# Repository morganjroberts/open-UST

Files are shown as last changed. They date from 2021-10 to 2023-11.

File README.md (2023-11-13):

<p align="center">
  
</p>

# **open-UST:** An Open Source Manufacturing Framework for a Low-cost Ultrasound Tomography Research System.

There is a high barrier to entry for researchers starting ultrasound tomography (UST) experiments: UST hardware is not available off the shelf, and custom systems are expensive.
The goal of the open-UST project is to **lower the barrier to entry for experimental UST researchers**, by providing a manufacturing framework that allows end users to build their own UST transducers in-house.

<p align="center">
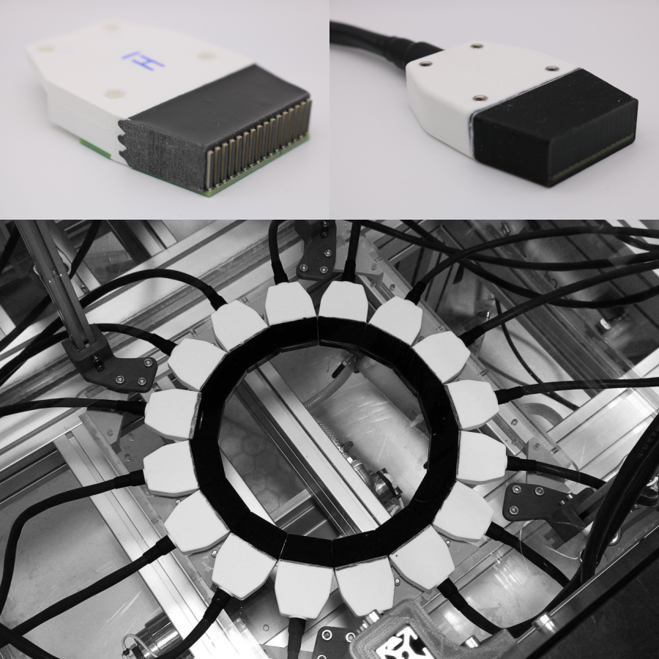
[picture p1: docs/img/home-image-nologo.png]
  
</p>

open-UST is part of an ongoing research project, guided by three objectives:

1. High accessibility for end users.
2. Nominal acoustic behaviour that supports UST imaging research.
3. Low inter-element variation (IEV) in acoustic behaviour.

## Features

- **Simple equipment requirements:** No specialist equipment required, only a 3D-printer, vacuum chamber and standard workshop tooling.
- **Low material cost:** ~£2k (excluding DAQ hardware) for a 256-element system.
- **Modular:** Both 2D and 3D imaging setups can be configured. 
- **Low interelement variation**: Recent testing showed that the individual sensing elements have uniform acoustic behaviour.
- **Other:**
  - Fully waterproof
  - Electromagnetically shielded
  - Transducer modules feature threaded mounting points for repeatable positioning
  - Includes option for a modular interface with the ITT Cannon DL5-260P connector (compatible with Verasonics)

## Hardware Distribution and Documentation

To access the design and manufacture files, clone this repository locally:

```
git clone https://github.com/morganjroberts/open-UST
```

The design and manufacture files are located in the `hardware-distribution` directory.

For the accompanying manufacturing documentation, please visit [morganjroberts.github.io/open-UST](https://morganjroberts.github.io/open-UST/).

## Citing open-UST

Please cite this article if you use open-UST in your research:

```
@article{roberts2023open,
  title     = {open-UST: An Open-Source Ultrasound Tomography Transducer Array System},
  author    = {Roberts, Morgan and Martin, Eleanor and Brown, Michael D and Cox, Ben T and Treeby, Bradley E},
  journal   = {IEEE Transactions on Ultrasonics, Ferroelectrics, and Frequency Control},
  year      = {2023},
  publisher = {IEEE},
  doi       = {10.1109/TUFFC.2023.3280635}
}
```

## Contact

open-UST is an ongoing research project from the [Biomedical Ultrasound Group](https://bug.medphys.ucl.ac.uk/) (University College London).

For questions, suggestions and feedback, please contact Morgan Roberts at [morgan.roberts.18@ucl.ac.uk](mailto:morgan.roberts.18@ucl.ac.uk).

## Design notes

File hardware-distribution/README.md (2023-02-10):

# Hardware Distribution

## CAD and 3D-printing files
- The CAD source files were generated in Fusion 360: [Download Fusion 360 for Education](https://www.autodesk.com/education/edu-software/overview?sorting=featured&filters=individual).
- The CAD source files are also available as `.step` files.
- The 3D-printed components have been exported as `.stl` files.

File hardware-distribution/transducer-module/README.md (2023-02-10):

# Transducer Module 

<p align="center">
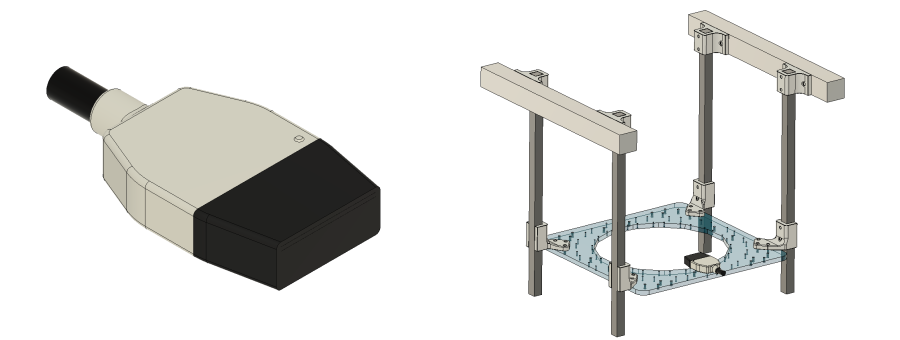
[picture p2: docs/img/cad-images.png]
  
</p>

The transducer module source files are found within `transducer-module.f3d`. The CAD file is split into the following components:

| Component | Type | Description |
|---|---|---|
| PZT Elements | Transducer part | PZT elements with matching layers.|
| PCB | Transducer part | Interconnect PCB used to interface cable with PZT elements. |
| Backing Layer | Transducer part | Cast behind the PZT elements to provide damping. |
| SMT Header | Transducer part | Surface mount header strip soldered to interconnect PCB to mate with cable IDC connector. |
| IDC connector | Transducer part | Crimped onto ribbon cable, mates with SMT header. |
| Housing | Transducer part | 3D-printed backbone of the transducer module. PCB and backing layers are bonded to this. Cable fixed to this. |
| Ribbon Cable | Transducer part | Round bundled ribbon cable in overall sheath. IDC connector is crimped to this. |
| Cover | Transducer part | Completes the housing after the cable is fixed in place. |
| PZT Alignment Mould | Sacrifical custom tooling | Aligns the PZT elements during manufacture, gets dissolved in water to remove it. |
| Clamp | Re-usable custom tooling | Clamps the housing to the base plate during backing layer casting. |
| Base Plate | Re-usable custom tooling | Holds the PCB, housing, and PZT alignment mould together during manufacture. |
| Mounting nuts | Transducer part | Glued into the housing, used to fix the transducer module to the array mounting plate. |
| Coatings | Transducer part | Epoxy and polyurethane coatings to protect the transducer modules. |
| Coating Moulds | Sacrificial custom tooling | Used for casting the coating layers around the transducer module. |
| Inclined Jig | Re-usable custom tooling | Used to hold the base plate at a 45 degree angle during application of conductive epoxy to the PZT electrodes. |
| Rigid Aperture Support | Additional part | Used to mount the transducer modules into a 2D ring array configuration. |
| Testing Mount | Additional part | Used to hold a single transducer module vertically during cable entry-point sealing, or electrical input impedance measurement. |
| Shielding Templates | Re-usable custom tooling | 2D templates to mark out the copper foil pattern nets electromagnetic shielding. |
| Coating Strong Plate | Re-usable custom tooling | Used to hold the coating moulds vertically and flat, to eliminate warping during casting. |
| Single Module Tank Mount | Additional part | Used to mount a single transducer module to an optical post for immersion in water e.g. for hydrophone scanning. |
| Storage Box | Additional part | Used to hold 8 transducer modules to protect their front faces from damage during storage. |

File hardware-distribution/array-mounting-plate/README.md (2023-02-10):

# Array Mounting Plate

<p align="center">
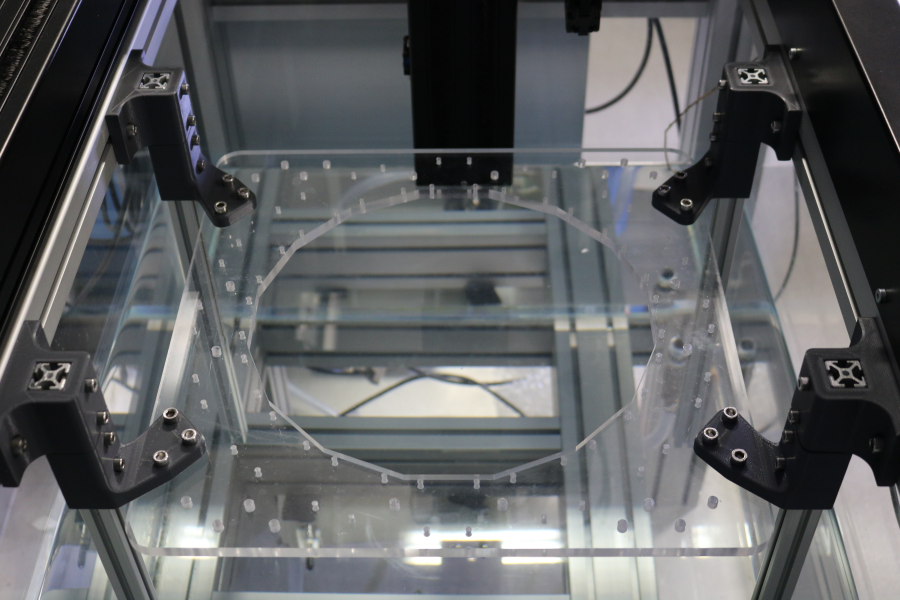
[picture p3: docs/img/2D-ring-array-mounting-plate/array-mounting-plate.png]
  
</p>

## Mounting Plate Design
- The original array mounting plate CAD object is found within the `transducer-module.f3d` source file, since the hole layout references the transducer geometry and parameters.
- `array-mounting-plate.step` and `array-mounting-plate.f3d` are also included but have no timeline history.

## Mounting Plate Manufacture

The array mounting plate is machined from 10 mm clear acrylic sheet, and uses precision-drilled holes to align the transducer modules.

- We CNC drilled this part, and the g-code was created using the "manufacture" tool in Fusion 360. The toolpaths are included in the `array-mounting-plate.f3d` file.
- Alternatively this part could be manually drilled. A to-scale `array-mounting-plate.pdf` file is included as a template, which could be printed at 100% size to assist with the hole layout.
- Alternatively, a laser cutter could be used to engrave the hole layout, using the `array-mounting-plate.dxf` file, and then the holes could be drilled.
- Fully laser cutting the holes is not recommended, since a drill bit is more precise.

## Rails and Brackets

- We mounted the array using aluminium extrusion rails and 3D-printed brackets.
- Designed for a rail spacing of 500 mm: [Precision Acoustics standard tank](https://www.acoustics.co.uk/product/ums-tank-specification/)
- The array mounting bracket CAD objects are found within the `transducer-module.f3d` source file within the `Rigid Aperture Support` component.
- The bracket `.stl` files are also included here.

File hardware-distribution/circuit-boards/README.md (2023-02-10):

# Printed Circuit Boards

## Manufacture Specifications:
- 2 layer
- 1.6 mm thickness FR4 (150 deg C)
- 1 oz (35 micrometer) Copper weight
- Immersion silver finish
- Solder resist

## Notes
- UK PCB fabrication house: [pcbtrain.co.uk/services/pcb-fabrication](https://www.pcbtrain.co.uk/services/pcb-fabrication)
- The source files (.pcb) were created in DesignSpark PCB: [rs-online.com/designspark/pcb-software](https://www.rs-online.com/designspark/pcb-software)
- The Gerber files have already been exported and are found in a subfolder for each PCB. 
- Gerber files can be viewed here: [pcbway.com/project/OnlineGerberViewer.html](https://www.pcbway.com/project/OnlineGerberViewer.html)
- For each PCB, package the Gerber files into a .zip folder and send to the pcb fabrication house.
- If you have modified the DesignSpark source files, you will need to re-generate the Gerber files: [pcbway.com/helpcenter/technical_support/How_to_generate_Gerber_files_from_DesignSpark.html](https://www.pcbway.com/helpcenter/technical_support/How_to_generate_Gerber_files_from_DesignSpark.html)

## Module Interconnect

- This PCB is located inside each transducer module.
- Interfaces the ribbon cable IDC connector with the individual PZT elements.

<p align="center">
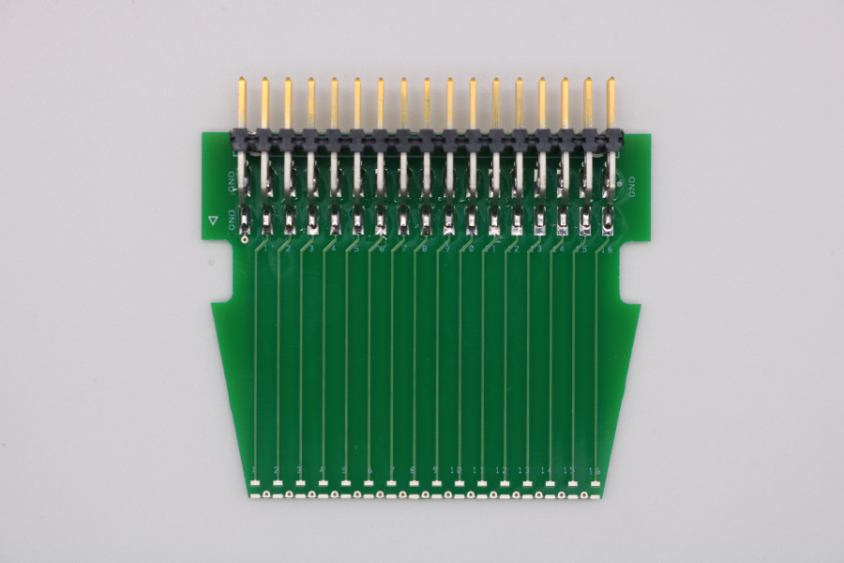
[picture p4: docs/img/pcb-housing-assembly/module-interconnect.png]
  
</p>

## Module Matching

- This PCB is located inside the plug backshell.
- Interfaces each ribbon cable IDC connector with the DL5-260PW6A breakout stack.
- Contains pads for single-inductor electrical impedance matching on every channel (unbalanced).
- A XX package 22 uH inductor is recommended.
- These pads should be filled with zero-ohm links if no matching is required.

<p align="center">
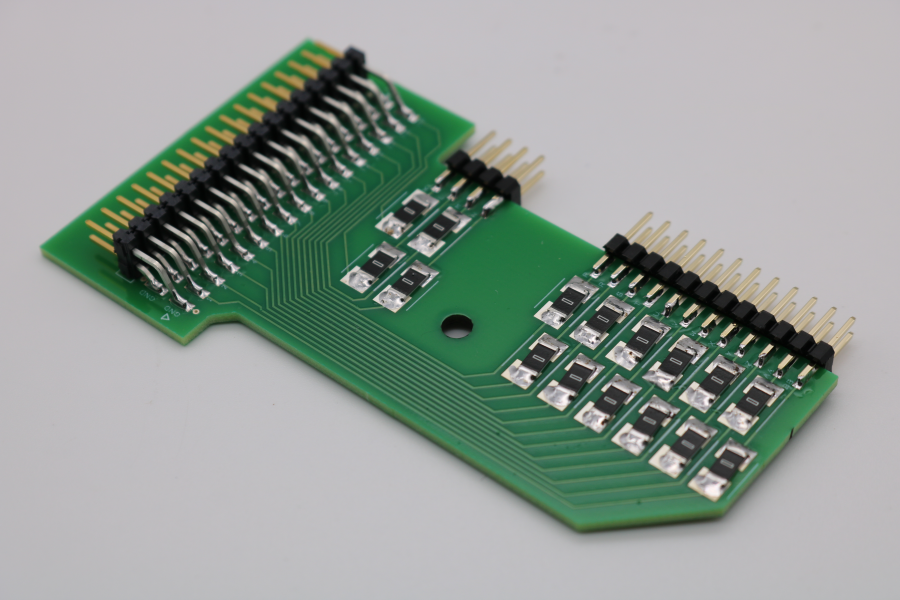
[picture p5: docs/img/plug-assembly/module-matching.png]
  
</p>

## DL5-260PW6A Breakout

- These PCBs form a stack that act as a breakout for the DL5-260PW6A plug connector.
- Provides a separate signal-ground pair for every channel (the plug pins share 2 ground pins per 8 signal pins).

<p align="center">
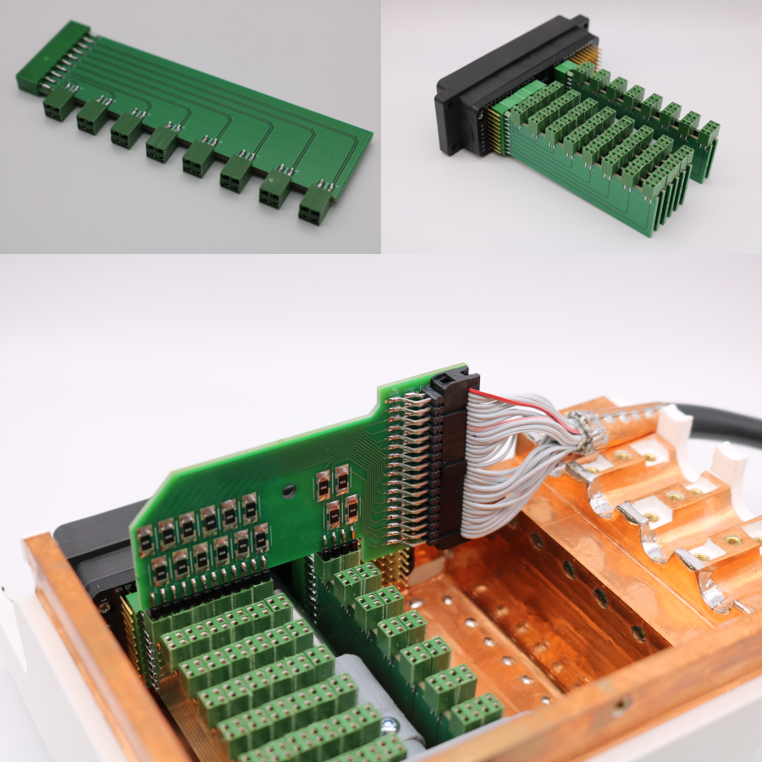
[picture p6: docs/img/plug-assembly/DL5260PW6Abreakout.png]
  
</p>

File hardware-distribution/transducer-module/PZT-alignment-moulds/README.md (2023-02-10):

# PZT Alignment Moulds

- The PZT alignment moulds have slots for accepting PZT elements.
- Width offsets are required to achieve a tight fit between the PZT element and the slot.
- Four stl files are included with different single-sided-width-offsets (sswo). A sswo is applied to each edge of the slot.

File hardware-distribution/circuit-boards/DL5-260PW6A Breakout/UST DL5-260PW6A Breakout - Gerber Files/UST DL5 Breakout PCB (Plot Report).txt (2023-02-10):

Plot Report
-----------

Report Written:     Tuesday, October 05, 2021
Design Path:        C:\Users\Morgan\Synology Drive\mySynologyDrive\Open source UST files\UST DL5 Breakout PCB.pcb
Design Title:       
Created:            28/09/2021 17:03:09
Last Saved:         05/10/2021 09:57:36
Editing Time:       8715 min
Units:              mm (precision 2)

Device Settings
===============

Gerber Settings
===============

    Leading zero suppression.
    G01 assumed throughout.
    Line termination <*> <CR> <LF>.
    3.5 format absolute inches.

    Format commands defined in Gerber file.
    Aperture table defined in Gerber file.
    Hardware arcs allowed.

Drill Settings
==============

    Excellon Format 1
    Format 3.5 absolute in inches.
    Zero suppression None

Plots Output
============

Gerber Output
=============

C:\Users\Morgan\Synology Drive\mySynologyDrive\Open source UST files\UST DL5 Breakout PCB - Top Copper.gbr

    Layers:
    --------------
    Top Copper

    D-Code Shape  (thou)
    -----------------------------------------------
    D90    Round 11.42
    D117   Round 10.00
    D120   Rectangle 39.37 X 157.48  Rotation 90
    D127   Round 12.00
    D129   Rectangle 39.37 X 78.74
    D130   Rectangle 39.37 X 157.48
    D131   Rectangle 39.37 X 78.74  Rotation 90

Gerber Output
=============

C:\Users\Morgan\Synology Drive\mySynologyDrive\Open source UST files\UST DL5 Breakout PCB - Top Copper (Paste).gbr

    Layers:
    --------------
    Top Copper

    D-Code Shape  (thou)
    -----------------------------------------------
    D122   Rectangle 35.37 X 153.48  Rotation 90
    D132   Rectangle 35.37 X 74.74
    D133   Rectangle 35.37 X 153.48
    D134   Rectangle 35.37 X 74.74  Rotation 90

Gerber Output
=============

C:\Users\Morgan\Synology Drive\mySynologyDrive\Open source UST files\UST DL5 Breakout PCB - Top Solder Mask.gbr

    Layers:
    -------------------
    Top Solder Mask

    D-Code Shape  (thou)
    -----------------------------------------------
    D124   Rectangle 45.37 X 163.48  Rotation 90
    D135   Rectangle 45.37 X 84.74
    D136   Rectangle 45.37 X 163.48
    D137   Rectangle 45.37 X 84.74  Rotation 90

Gerber Output
=============

C:\Users\Morgan\Synology Drive\mySynologyDrive\Open source UST files\UST DL5 Breakout PCB - Top Silkscreen.gbr

    Layers:
    ------------------
    Top Silkscreen

    D-Code Shape  (thou)
    -----------------------
    D84    Round 1.00
    D127   Round 12.00

Gerber Output
=============

C:\Users\Morgan\Synology Drive\mySynologyDrive\Open source UST files\UST DL5 Breakout PCB - Bottom Copper.gbr

    Layers:
    -----------------
    Bottom Copper

    D-Code Shape  (thou)
    -----------------------------------------------
    D90    Round 11.42
    D117   Round 10.00
    D120   Rectangle 39.37 X 157.48  Rotation 90
    D127   Round 12.00
    D129   Rectangle 39.37 X 78.74
    D130   Rectangle 39.37 X 157.48
    D131   Rectangle 39.37 X 78.74  Rotation 90

Gerber Output
=============

C:\Users\Morgan\Synology Drive\mySynologyDrive\Open source UST files\UST DL5 Breakout PCB - Bottom Copper (Paste).gbr

    Layers:
    -----------------
    Bottom Copper

    D-Code Shape  (thou)
    -----------------------------------------------
    D122   Rectangle 35.37 X 153.48  Rotation 90
    D132   Rectangle 35.37 X 74.74
    D133   Rectangle 35.37 X 153.48
    D134   Rectangle 35.37 X 74.74  Rotation 90

Gerber Output
=============

C:\Users\Morgan\Synology Drive\mySynologyDrive\Open source UST files\UST DL5 Breakout PCB - Bottom Solder Mask.gbr

    Layers:
    ----------------------
    Bottom Solder Mask

    D-Code Shape  (thou)
    -----------------------------------------------
    D124   Rectangle 45.37 X 163.48  Rotation 90
    D135   Rectangle 45.37 X 84.74
    D136   Rectangle 45.37 X 163.48
    D137   Rectangle 45.37 X 84.74  Rotation 90

Gerber Output
=============

C:\Users\Morgan\Synology Drive\mySynologyDrive\Open source UST files\UST DL5 Breakout PCB - Bottom Silkscreen.gbr

    Layers:
    ---------------------
    Bottom Silkscreen

    D-Code Shape  (thou)
    -----------------------
    D84    Round 1.00
    D127   Round 12.00

Gerber Output
=============

C:\Users\Morgan\Synology Drive\mySynologyDrive\Open source UST files\UST DL5 Breakout PCB - Gerber Drill Data - [Through Hole].gbr

    Layers:
    ------------------
    [Through Hole]

    D-Code Shape  (thou)
    -----------------------

NC Drill Output
===============

C:\Users\Morgan\Synology Drive\mySynologyDrive\Open source UST files\UST DL5 Breakout PCB - NC Drill Data - [Through Hole].drl

    Output:
    -----------------------------
    Plated Round Drill Holes
    Unplated Round Drill Holes
    Plated Slots
    Unplated Slots

    Tool  Size Count   ID
    ----------------------------
    ----------------------------
    Total      0
    ----------------------------

Gerber Output
=============

C:\Users\Morgan\Synology Drive\mySynologyDrive\Open source UST files\UST DL5 Breakout PCB - Drill Ident Drawing - [Through Hole].gbr

    Layers:
    ------------------
    [Through Hole]

Drill Ident Drawing
===================

    Drill Plated Size Shape ID
    -----------------------------------

    D-Code Shape  (thou)
    -----------------------

Gerber Output
=============

C:\Users\Morgan\Synology Drive\mySynologyDrive\Open source UST files\UST DL5 Breakout PCB - Outline.gbr

    Layers:
    ------------------
    Board Outlines

    D-Code Shape  (thou)
    -----------------------
    D127   Round 12.00

End Of Report.

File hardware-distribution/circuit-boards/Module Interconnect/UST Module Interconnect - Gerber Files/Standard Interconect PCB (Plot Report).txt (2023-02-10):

Plot Report
-----------

Report Written:     Tuesday, October 05, 2021
Design Path:        C:\Users\Morgan\Synology Drive\mySynologyDrive\Open source UST files\Standard Interconect PCB.pcb
Design Title:       
Created:            28/02/2020 11:32:59
Last Saved:         05/10/2021 09:57:34
Editing Time:       10156 min
Units:              mm (precision 2)

Device Settings
===============

Gerber Settings
===============

    Leading zero suppression.
    G01 assumed throughout.
    Line termination <*> <CR> <LF>.
    3.5 format absolute inches.

    Format commands defined in Gerber file.
    Aperture table defined in Gerber file.
    Hardware arcs allowed.

Drill Settings
==============

    Excellon Format 1
    Format 3.5 absolute in inches.
    Zero suppression None

Plots Output
============

Gerber Output
=============

C:\Users\Morgan\Synology Drive\mySynologyDrive\Open source UST files\Standard Interconect PCB - Top Documentation.gbr

    Layers:
    ---------------------
    Top Documentation

    D-Code Shape  (thou)
    -----------------------
    D85    Round 3.94

Gerber Output
=============

C:\Users\Morgan\Synology Drive\mySynologyDrive\Open source UST files\Standard Interconect PCB - Top Silkscreen.gbr

    Layers:
    ------------------
    Top Silkscreen

    D-Code Shape  (thou)
    -----------------------
    D10    Round 5.00
    D12    Round 19.69
    D84    Round 1.00
    D85    Round 3.94

Gerber Output
=============

C:\Users\Morgan\Synology Drive\mySynologyDrive\Open source UST files\Standard Interconect PCB - Top Copper.gbr

    Layers:
    --------------
    Top Copper

    D-Code Shape  (thou)
    ----------------------------------------------
    D89    Round 31.50
    D90    Round 11.42
    D108   Rectangle 19.69 X 39.37  Rotation 90
    D109   Rectangle 50.00 X 125.20
    D110   Round 105.12

Gerber Output
=============

C:\Users\Morgan\Synology Drive\mySynologyDrive\Open source UST files\Standard Interconect PCB - Top Copper (Paste).gbr

    Layers:
    --------------
    Top Copper

    D-Code Shape  (thou)
    ----------------------------------------------
    D111   Rectangle 15.69 X 35.37  Rotation 90
    D112   Rectangle 46.00 X 121.20

Gerber Output
=============

C:\Users\Morgan\Synology Drive\mySynologyDrive\Open source UST files\Standard Interconect PCB - Top Solder Mask.gbr

    Layers:
    -------------------
    Top Solder Mask

    D-Code Shape  (thou)
    ----------------------------------------------
    D113   Round 37.50
    D114   Rectangle 25.69 X 45.37  Rotation 90
    D115   Rectangle 56.00 X 131.20
    D116   Round 111.12

Gerber Output
=============

C:\Users\Morgan\Synology Drive\mySynologyDrive\Open source UST files\Standard Interconect PCB - Bottom Copper.gbr

    Layers:
    -----------------
    Bottom Copper

    D-Code Shape  (thou)
    -----------------------
    D10    Round 5.00
    D89    Round 31.50
    D110   Round 105.12
    D117   Round 10.00

Gerber Output
=============

C:\Users\Morgan\Synology Drive\mySynologyDrive\Open source UST files\Standard Interconect PCB - Bottom Copper (Paste).gbr

    Layers:
    -----------------
    Bottom Copper

    D-Code Shape  (thou)
    -----------------------

Gerber Output
=============

C:\Users\Morgan\Synology Drive\mySynologyDrive\Open source UST files\Standard Interconect PCB - Bottom Solder Mask.gbr

    Layers:
    ----------------------
    Bottom Solder Mask

    D-Code Shape  (thou)
    -----------------------
    D113   Round 37.50
    D116   Round 111.12

Gerber Output
=============

C:\Users\Morgan\Synology Drive\mySynologyDrive\Open source UST files\Standard Interconect PCB - Gerber Drill Data - [Through Hole].gbr

    Layers:
    ------------------
    [Through Hole]

    D-Code Shape  (thou)
    -----------------------
    D118   Round 11.81
    D119   Round 70.08

NC Drill Output
===============

C:\Users\Morgan\Synology Drive\mySynologyDrive\Open source UST files\Standard Interconect PCB - NC Drill Data - [Through Hole].drl

    Output:
    -----------------------------
    Plated Round Drill Holes
    Unplated Round Drill Holes
    Plated Slots
    Unplated Slots

    Tool  Size           Count   ID
    --------------------------------------
    T001  0.01181 inches 33    V
    T002  0.07008 inches 2     Z
    --------------------------------------
    Total                35
    --------------------------------------

Gerber Output
=============

C:\Users\Morgan\Synology Drive\mySynologyDrive\Open source UST files\Standard Interconect PCB - Drill Ident Drawing - [Through Hole].gbr

    Layers:
    ------------------
    [Through Hole]

Drill Ident Drawing
===================

    Drill Plated Size Shape ID
    -----------------------------------
    12    Y      100  Round V
    70    Y      100  Round Z

    D-Code Shape  (thou)
    -----------------------
    D10    Round 5.00
    D83    Round 100.00

Gerber Output
=============

C:\Users\Morgan\Synology Drive\mySynologyDrive\Open source UST files\Standard Interconect PCB - Outline.gbr

    Layers:
    ------------------
    Board Outlines

    D-Code Shape  (thou)
    -----------------------
    D10    Round 5.00

End Of Report.

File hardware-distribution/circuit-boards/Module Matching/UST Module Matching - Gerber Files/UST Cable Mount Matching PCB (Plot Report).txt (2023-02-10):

Plot Report
-----------

Report Written:     Tuesday, October 05, 2021
Design Path:        C:\Users\Morgan\Synology Drive\mySynologyDrive\Open source UST files\UST Cable Mount Matching PCB.pcb
Design Title:       
Created:            28/09/2021 18:44:46
Last Saved:         05/10/2021 09:57:35
Editing Time:       9563 min
Units:              mm (precision 2)

Device Settings
===============

Gerber Settings
===============

    Leading zero suppression.
    G01 assumed throughout.
    Line termination <*> <CR> <LF>.
    3.5 format absolute inches.

    Format commands defined in Gerber file.
    Aperture table defined in Gerber file.
    Hardware arcs allowed.

Drill Settings
==============

    Excellon Format 1
    Format 3.5 absolute in inches.
    Zero suppression None

Plots Output
============

Gerber Output
=============

C:\Users\Morgan\Synology Drive\mySynologyDrive\Open source UST files\UST Cable Mount Matching PCB - Top Copper.gbr

    Layers:
    --------------
    Top Copper

    D-Code Shape  (thou)
    -----------------------------------------------
    D89    Round 31.50
    D90    Round 11.42
    D109   Rectangle 50.00 X 125.20
    D110   Round 105.12
    D120   Rectangle 39.37 X 157.48  Rotation 90
    D121   Rectangle 118.11 X 137.80

Gerber Output
=============

C:\Users\Morgan\Synology Drive\mySynologyDrive\Open source UST files\UST Cable Mount Matching PCB - Top Copper (Paste).gbr

    Layers:
    --------------
    Top Copper

    D-Code Shape  (thou)
    -----------------------------------------------
    D112   Rectangle 46.00 X 121.20
    D122   Rectangle 35.37 X 153.48  Rotation 90
    D123   Rectangle 114.11 X 133.80

Gerber Output
=============

C:\Users\Morgan\Synology Drive\mySynologyDrive\Open source UST files\UST Cable Mount Matching PCB - Top Solder Mask.gbr

    Layers:
    -------------------
    Top Solder Mask

    D-Code Shape  (thou)
    -----------------------------------------------
    D113   Round 37.50
    D115   Rectangle 56.00 X 131.20
    D116   Round 111.12
    D124   Rectangle 45.37 X 163.48  Rotation 90
    D125   Round 143.80
    D126   Rectangle 124.11 X 143.80

Gerber Output
=============

C:\Users\Morgan\Synology Drive\mySynologyDrive\Open source UST files\UST Cable Mount Matching PCB - Top Silkscreen.gbr

    Layers:
    ------------------
    Top Silkscreen

    D-Code Shape  (thou)
    -----------------------
    D10    Round 5.00
    D12    Round 19.69
    D84    Round 1.00
    D85    Round 3.94

Gerber Output
=============

C:\Users\Morgan\Synology Drive\mySynologyDrive\Open source UST files\UST Cable Mount Matching PCB - Documentation.gbr

    Layers:
    -----------------
    Documentation

    D-Code Shape  (thou)
    -----------------------
    D85    Round 3.94
    D127   Round 12.00

Gerber Output
=============

C:\Users\Morgan\Synology Drive\mySynologyDrive\Open source UST files\UST Cable Mount Matching PCB - Bottom Copper.gbr

    Layers:
    -----------------
    Bottom Copper

    D-Code Shape  (thou)
    -----------------------------------------------
    D89    Round 31.50
    D110   Round 105.12
    D117   Round 10.00
    D120   Rectangle 39.37 X 157.48  Rotation 90
    D127   Round 12.00

Gerber Output
=============

C:\Users\Morgan\Synology Drive\mySynologyDrive\Open source UST files\UST Cable Mount Matching PCB - Bottom Copper (Paste).gbr

    Layers:
    -----------------
    Bottom Copper

    D-Code Shape  (thou)
    -----------------------------------------------
    D122   Rectangle 35.37 X 153.48  Rotation 90

Gerber Output
=============

C:\Users\Morgan\Synology Drive\mySynologyDrive\Open source UST files\UST Cable Mount Matching PCB - Bottom Solder Mask.gbr

    Layers:
    ----------------------
    Bottom Solder Mask

    D-Code Shape  (thou)
    -----------------------------------------------
    D113   Round 37.50
    D116   Round 111.12
    D124   Rectangle 45.37 X 163.48  Rotation 90
    D125   Round 143.80

Gerber Output
=============

C:\Users\Morgan\Synology Drive\mySynologyDrive\Open source UST files\UST Cable Mount Matching PCB - Gerber Drill Data - [Through Hole].gbr

    Layers:
    ------------------
    [Through Hole]

    D-Code Shape  (thou)
    -----------------------
    D118   Round 11.81
    D119   Round 70.08
    D128   Round 137.80

NC Drill Output
===============

C:\Users\Morgan\Synology Drive\mySynologyDrive\Open source UST files\UST Cable Mount Matching PCB - NC Drill Data - [Through Hole].drl

    Output:
    -----------------------------
    Plated Round Drill Holes
    Unplated Round Drill Holes
    Plated Slots
    Unplated Slots

    Tool  Size           Count   ID  (Plated/Unplated)
    -----------------------------------------------------------
    T001  0.01181 inches 18    V
    T002  0.07008 inches 2     Z
    T003  0.13780 inches 1     /AA
    -----------------------------------------------------------
    Total                21
    -----------------------------------------------------------

Gerber Output
=============

C:\Users\Morgan\Synology Drive\mySynologyDrive\Open source UST files\UST Cable Mount Matching PCB - Drill Ident Drawing - [Through Hole].gbr

    Layers:
    ------------------
    [Through Hole]

Drill Ident Drawing
===================

    Drill Plated Size Shape ID
    -----------------------------------
    12    Y      100  Round V
    70    Y      100  Round Z
    138          100  Round AA

    D-Code Shape  (thou)
    -----------------------
    D10    Round 5.00
    D83    Round 100.00

Gerber Output
=============

C:\Users\Morgan\Synology Drive\mySynologyDrive\Open source UST files\UST Cable Mount Matching PCB - Outline.gbr

    Layers:
    ------------------
    Board Outlines

    D-Code Shape  (thou)
    -----------------------
    D127   Round 12.00

End Of Report.

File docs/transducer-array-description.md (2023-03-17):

# System Description

Each transducer module is a 16-element linear array, with complete electromagnetic shielding and waterproofing. The standard 256-element open-UST imaging system is formed by assembling 16 of these modules into a ring array.

Each module has the following specifications:

- Ring array diameter: 220 mm
- PZT elevation height: 10 mm
- PZT lateral width: 1 mm
- PZT thickness: 1 mm
- PZT pitch: 2.54 mm
- Transmit-Receive watershot data characteristics (N = 256):
    - Resonance frequency: 1.21 MHz \( \pm \) 7.1 kHz
    - Amplitude deviation at resonance: 7.9%
    - 6 dB FBW (1.08 MHz - 1.41 MHz): 29% \( \pm \) 6.1%
    - 12 dB FBW (924 kHz - 1.58 MHz): 54% \( \pm \) 4.9%
    - 40 dB  FBW (528 kHz - 2.61 MHz): 170% \( \pm \) 3.0%
    - Signal to noise ratio: 61.2 dB \( \pm \) 1.2 dB
    - Receive cross talk: -37.1 dB \( \pm \) 6.0 dB
- Beam Pattern (N = 64):
    - Elevational skew: 0.457\(^{\circ} \pm \) 0.207\(^{\circ} \)
    - Lateral skew: 1.169\(^{\circ} \pm \) 0.834\(^{\circ} \)
    - Elevational -6 dB beamwidth: 16.3 mm \( \pm \) 0.456 mm
    - Lateral -6 dB opening angle: 55.4\(^{\circ} \pm \) 2.96\(^{\circ} \)
- Electrical Input Impedance (N = 128):
    - Phase at resonance: -8.58\(^{\circ} \pm \) 4.96\(^{\circ} \)
    - Magnitude at resonance: 1114 \(\Omega \pm \) 121 \(\Omega \)

## Further Reading

- M. Roberts, E. Martin, M. Brown, B. Cox and B. Treeby, "Transducer Module Development for an Open-Source Ultrasound Tomography System," 2021 IEEE International Ultrasonics Symposium (IUS), 2021, pp. 1-4, doi: [10.1109/IUS52206.2021.9593866](https://doi.org/10.1109/IUS52206.2021.9593866) Available for download [here](http://gofile.me/3oqCv/ncMDqJbop)
- M. Roberts, E. Martin, M. Brown, B. Cox and B. Treeby, "Matching Layer Deposition for an Open-Source Ultrasound Tomography System: Inter-Element Variation in Frequency Response," 2022 IEEE International Ultrasonics Symposium (IUS), 2022, pp. 1-4, doi: [10.1109/IUS54386.2022.9957739](https://doi.org/10.1109/IUS54386.2022.9957739) Available for download [here](http://gofile.me/3oqCv/6K82Qo7WL)
- Roberts, Morgan, Eleanor Martin, Michael D. Brown, Ben T. Cox, and Bradley E. Treeby. "open-UST: An Open-Source Ultrasound Tomography Transducer Array System." arXiv preprint arXiv:2302.10114 (2023) doi: [10.48550/arXiv.2302.10114](https://doi.org/10.48550/arXiv.2302.10114)

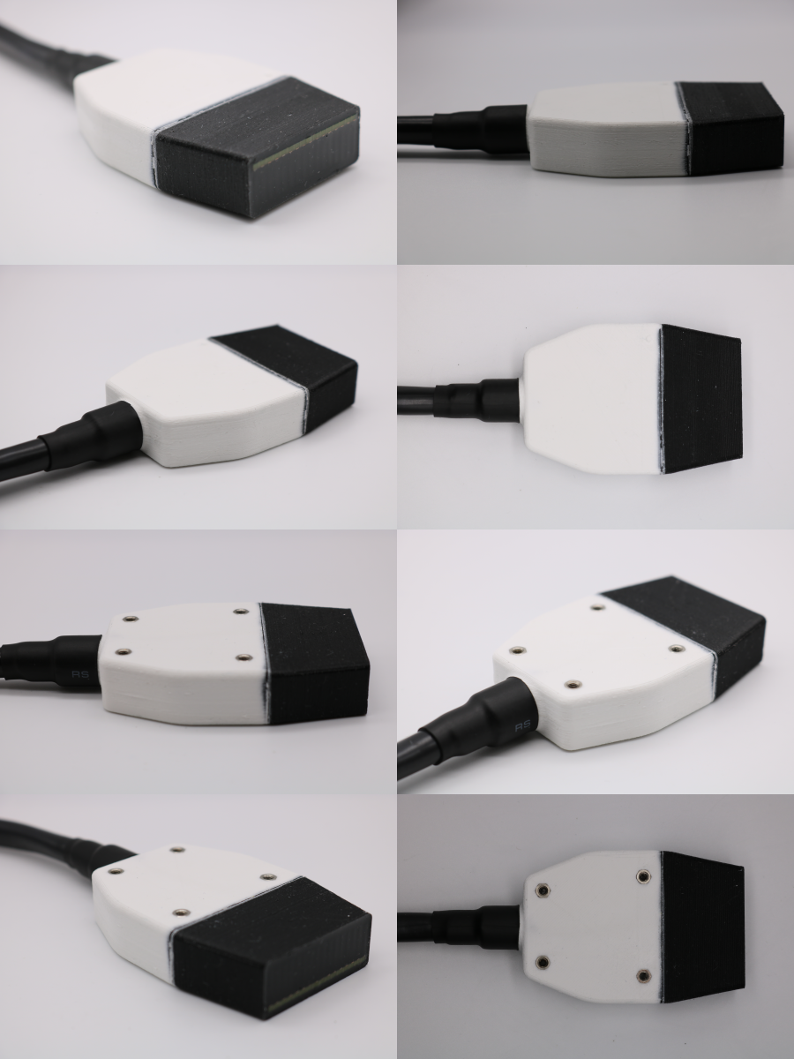
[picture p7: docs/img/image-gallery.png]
image-gallery


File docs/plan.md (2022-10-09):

# MVP

Outputs
- section pages w/photos DRAFTED
- home page DRAFTED
- contact page DRAFTED
- breast ultrasound with UST overview/background NOT DONE
- further reading NOT DONE
  - IUS video links embeded
- readme on repo - this is just the home/about page.
- add overview section to each page
- getting started page

Next most important is adding pictures

------------------------------------------------------------
WIP pages
----------
custom tooling
calibration
impedance measurement
impedance circuit
2d mounting plate/tank

------------------------------------------------------------
to link pages to sections in other pages
[see_link](custom-tooling-manufacture.md#test1)

------------------------------------------------------------
hardware
- files
- BOM - unify part numbers throughout docs
- 3d print orientation and settings files
- plug wiring diagram
- matlab functions for polymer casting
---------------------------------------------------------------
things to check
- safety
- capitalisation in titles and subtitles.
- hyphenation
- full stops vs commas at end of lines
- unify 'notes' formating
- standard sentences
  - (orientation and slicer settings detailed in [3D-print-spec.pdf](https://github.com/morganjroberts/open-UST/blob/main/hardware-distribution/3D-print-spec.pdf))
  - (offset calibration process described [here](dimension-calibration-3D-printing.md#deposition-mould))
  - (further details [here](custom-tooling-manufacture.md))
- standard sentence for threaded inserts
- spell check
- unify abrasive-paper vs sandpaper.
- check bullet point consistency make all '1.'
- unify titles match nav
- polarity section makes sense with oictures ink markings

---------------------------------------------------------------

# issues
#1 `tungstenPolymerRatio`
#2 deposition jig
#3 probe assignment concept
#3 add BOM ID numbers throughout documentation
#4 add short overview to each section
#5 CAD flythrough video 
#7 add images to about page
#8 license
#9 add a gentting started page
#10 future work page - klm modelling - transducer design - right angled format
#11 DL5 pinout diagrams

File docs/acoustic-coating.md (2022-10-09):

# Acoustic Coating

## Aptflex F7 Polyurethane Preparation

- **Note:** The working time of aptflex F7 is 20 minutes. Beyond this its viscosity will increase as the reaction progresses, making it difficult to work with the aptflex F7. Do not attempt to coat more than two modules in one batch (it takes 5-8 minutes to coat each module).
- **Note:** Use aa fumehood when working with the polyurethane.
- **Note:** Degreasing was performed previously, do not repeat it as the liquid solvent could dissolve the surrounding PVA mould material and deposit a thin layer of PVA on the transducer front face
- **Note:** The final vacuum achieved by the pump/chamber must be better than 5 mbar.

Prepare the polyurethane using the following procedure:

1. Clean a safety blade and a sewing needle using a paper towel soaked in isopropyl alcohol. Set aside on a clean surface.
1. Use an air duster to remove debris from the front face of the transducer module.
1. Test the fit of the 15ga blunt needle in the coating cavity.
1. If the needle is slightly too large, compress it in a vice until it fits.
1. Tightly push the needle luer-slip fitting onto the 60 ml syringe body and remove the plunger.
1. Calculate the required mass of part A and part B. For two transducer modules, the required volume is ~40 ml, and the required quantities (with a 6:1 weight ratio) are:

| Component | Mass [g] |
|-----------|----------|
|Part A |36|
|Part B |6|

1. Place a clean mixing pot (minimum capacity 250 ml) on a digital balance (resolution 0.1 g or better), and tare it.
1. Dispense the required mass of part A.
1. Tare the balance.
1. Dispense the required mass of part B.
1. Use a plastic rod to mix the components together for 5 minutes. Frequently scrape down the walls and bottom of the pot to make sure that all of the material is fully incorporated.
1. Place the mixing pot into a vacuum chamber, seal the lid.
1. Turn on the vacuum pump.
1. Once the mixture has expanded and collapsed, releasing the trapped air, all the pump to run for 20 more seconds.
1. Turn off the pump and release the vacuum.

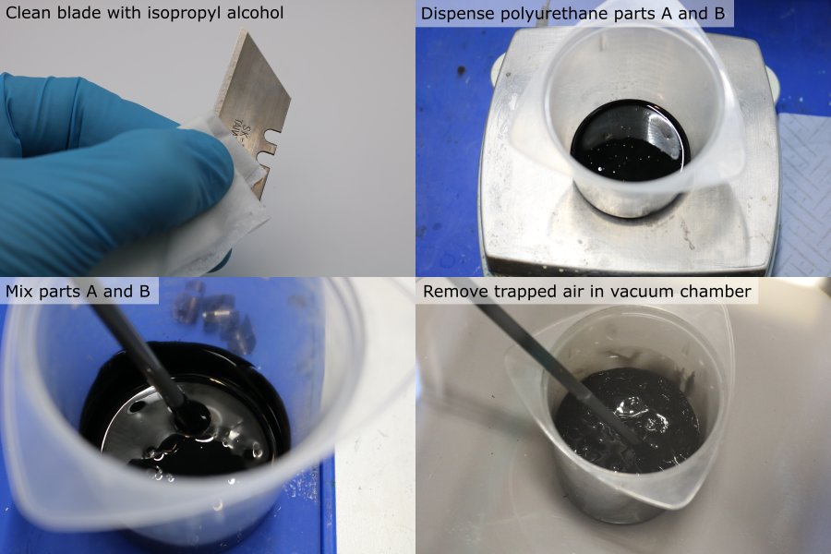
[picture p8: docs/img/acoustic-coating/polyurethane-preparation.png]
polyurethane-preparation


## Polyurethane Casting: Sides

1. Remove the pot from the vacuum chamber and bring it into contact with the syringe barrel opening.
1. Slowly, pour the mixture into the syringe.
1. Holding the syringe horiztonally, push the plunger into the syringe barrel until it forms a seal, but no further.
1. Gently rotate the syringe so that it is vertical, with the needle facing up, and allow the mixture to settle and for the air to rise to the top.
1. Slowly push the plunger to expell all of the air from the syringe.
1. Carefully place the needle into the coating mould cavity, as far down as it will go (it may be necessary to wiggle the needle if the fit is tight).
1. Push the syringe plunger to dispense the polyurethane into the mould. Due to its viscosity, this can take 3-5 minutes.
1. Once the polyurethane has reached the top of the mould, gently remove the needle from the mould.

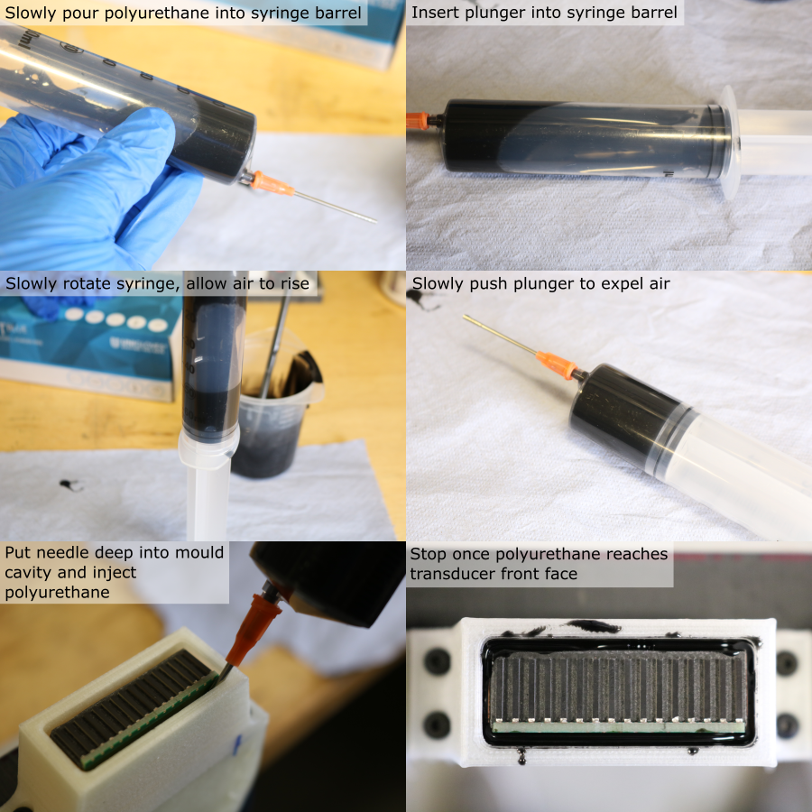
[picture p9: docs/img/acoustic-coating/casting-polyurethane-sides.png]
casting-polyurethane-sides


## Polyurethane Casting: Front Face
1. With the needle almost in contact with the PZT elements, dispense a layer of polyurethane onto the transducer front face. 
1. Use the pre-cleaned safety blade to remove the excess polyurethane. Holding it at a 45° angle, slowly drag it along the surface of the coating mould, at a rate of ~1 mm/s.
1. Use the pre-cleaned sewing needle to remove pockets of air trapped between the PZT elements. Gently agitate the polyurethane between the elements so that it fully contacts the backing layer and the PCB.
1. Remove excess polyurethane once more using the safety blade.
1. Allow the polyurethane to cure for 48 hours.

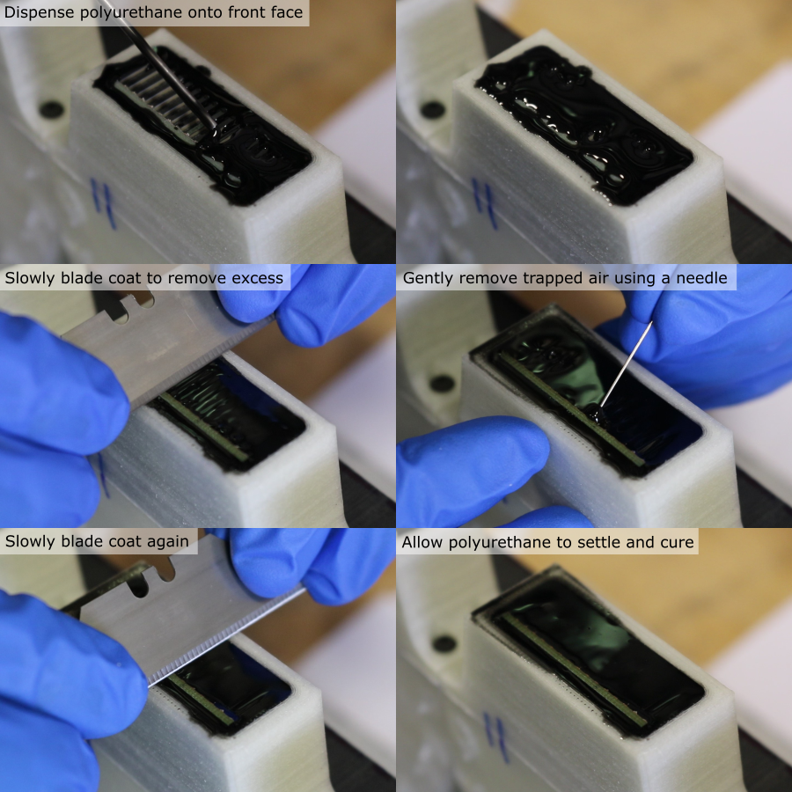
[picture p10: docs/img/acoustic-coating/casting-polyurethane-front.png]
casting-polyurethane-front


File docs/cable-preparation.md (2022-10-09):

# Cable Preparation

A shielded round ribbon cable is used to connect each transducer module to the data acquisition system. The ends of each cable must be prepared by installing an insulation-displaement-contact (IDC) connector, and by terminating the copper braid.

## Cut Cable to Length

* Cut enough cable so that there is enough slack when the transducer modules are connected to the data acquisition system, and placed in the water tank.
* For this system, 2.3 m was the required length.
* Up to 122 mm of cable may need to be removed when the sheath length is adjusted (see below).
* To account for this the cables were cut oversized, to lengths of 2.5 m.

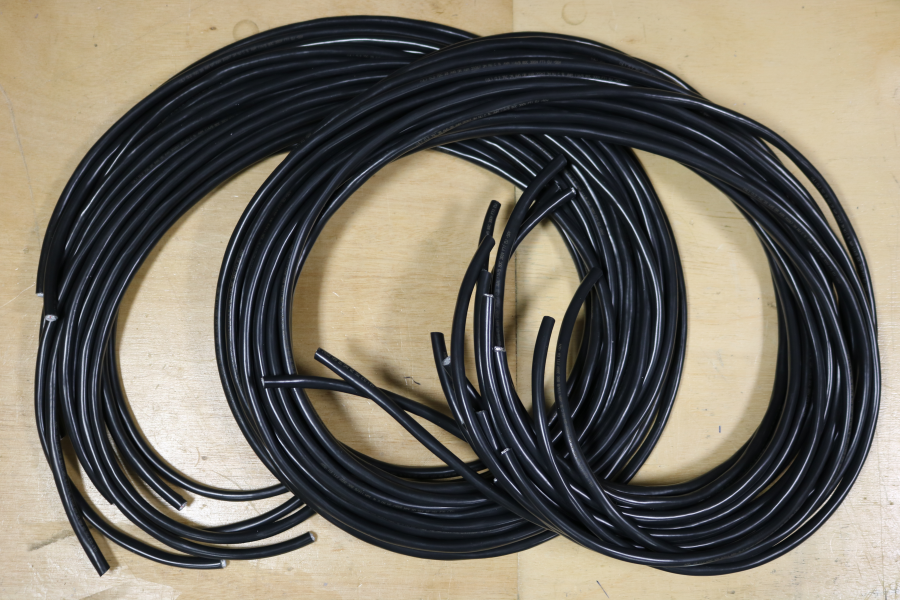
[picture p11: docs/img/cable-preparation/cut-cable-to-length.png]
cut-cable-to-length


## Braid Preparation

The cable braid is made from groups of strands that are woven together. To prevent the braid from becoming untangled later, each group of strands should be terminated with solder.

1. Setup a soldering iron with a temperature of 350 °C and a small tip.
1. Remove 25 mm of sheath using a scalpel. Bend the cable to put tension on the sheath. Use a fresh, sharp blade with light, shallow strokes. Take care not to cut the braid wires underneath the sheath. 
1. For a group of braid strands, use tweezers to pull the group free from the braid.
1. Twist the end of the group together.
1. Apply a small amount of solder to the end of the group of strands.
1. Bend the group of strands down.
1. Repeat for all groups of braid strands.

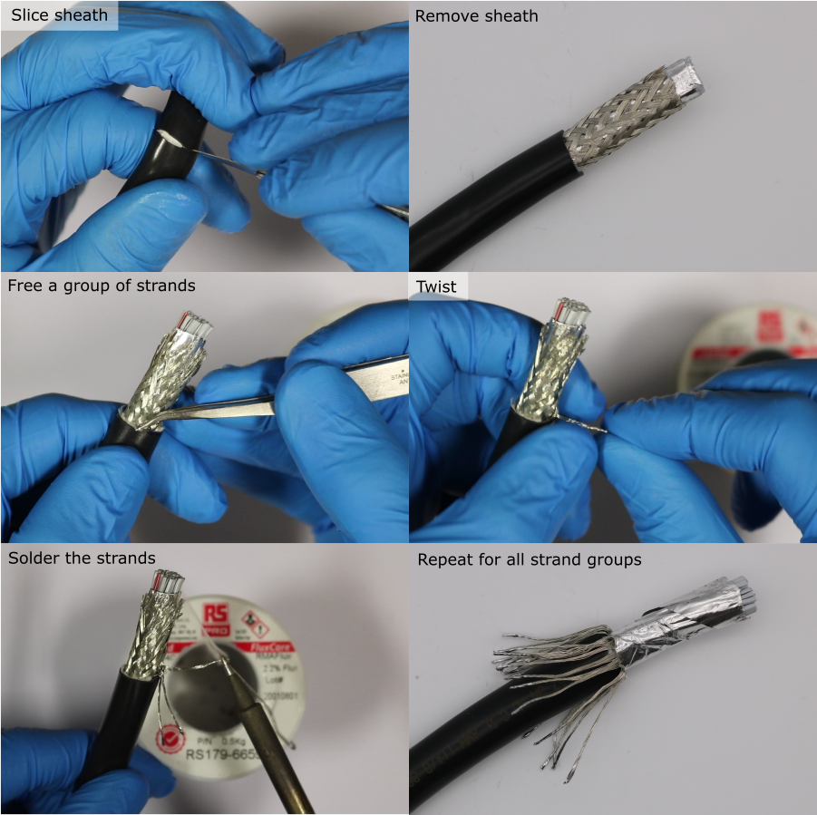
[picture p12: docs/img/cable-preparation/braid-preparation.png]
braid-preparation


## Adjusting the Sheath Length

The length of ribbon cable between the end of the sheath and the IDC connector should be 36 mm \( \pm \) 5 mm. Deviations from this will make it difficult to install the cable into the transducer module later.

The ribbon cable has a continuous split/bonded repeating pattern, where the split sections are 36 mm in length, and the bonded sections are 25 mm in length , detailed in [`3M-3659-3_34-way-screened-round-ribbon-cable_datasheet.pdf`](https://github.com/morganjroberts/open-UST/blob/main/hardware-distribution/technical-datasheets/3M-3659-3_34-way-screened-round-ribbon-cable_datasheet.pdf))

The IDC connector is installed on the bonded section. The end of the sheath should be aligned with the point where the ribbon cable changes from bonded to split (moving towards the end of the cable). This will provide approximately 36 mm of cable between the end of the sheath and the IDC connector. 

1. Use a scalpel to remove the foil, exposing the ribbon cable.
1. Mark the transition point where the ribbon cable changes from split to bonded (moving towards the end of the cable) using a permenant marker. If this point is not visible, remove sheath in small increments until it is visible. There must be at least 10 mm of bonded section for installing the IDC connectors. If there is less than 6 mm, remove more sheath to find a new transition point.
1. Make a mark 36 mm back from this transition point, using a permenant marker.
1. Use a scalpel to remove the remaining sheath up to this mark.
1. Pull back the braid to expose the foil.
1. Use a scalpel to remove the foil, exposing the ribbon cable. Verify that the end of the sheath is aligned with the point where the ribbon cable changes from bonded to split (moving towards the end of the cable).

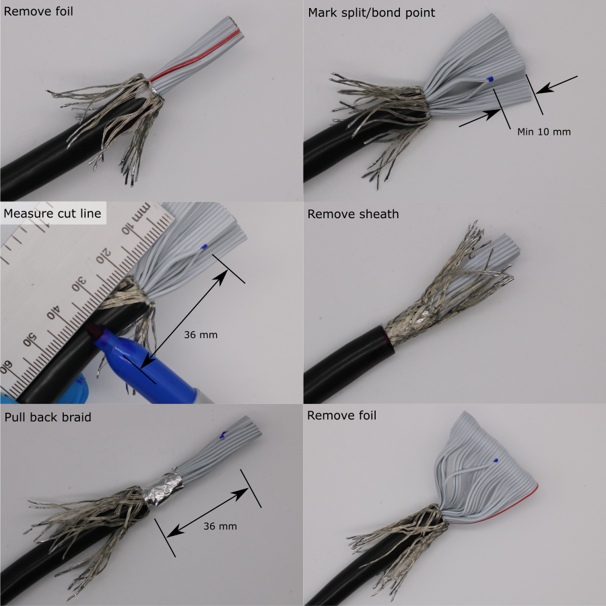
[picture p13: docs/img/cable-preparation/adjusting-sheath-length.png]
adjusting-sheath-length


## Installing the Connectors

1. Orient the cable so that the red wire is on the right hand side.
1. Pre-flatten the ribbon cable by folding it approximately 6 mm above the transition from split to bonded.
1. Install the IDC clip underneath the cable. 
1. Install the IDC housing onto the IDC clip. Press the two parts together until the IDC contacts grip the ribbon cable. Make sure that the polarity indicator (embossed triangle) is on the right hand side. The tab should also be facing forwards. Make sure the individual conductors are well aligned with the clip indentations and the IDC contacts.
1. Use a vice to compress the assembly until the IDC clip locks to the IDC housing.
1. Use side cutters to trim the excess ribbon cable flush with the IDC connector.

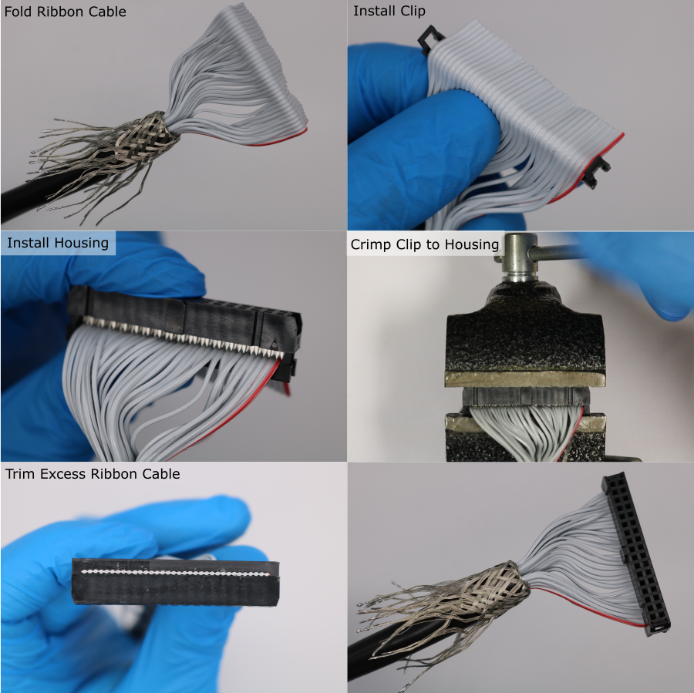
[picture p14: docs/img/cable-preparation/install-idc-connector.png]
install-idc-connector


## Test Continuity and Isolation

The IDC connector installation should be verified at this point, to prevent further manufacture on a bad cable, which would have to be repeated once the fault is detected.
Conductor continuity along the cable is tested, in addition to isolation between neighbouring conductors.

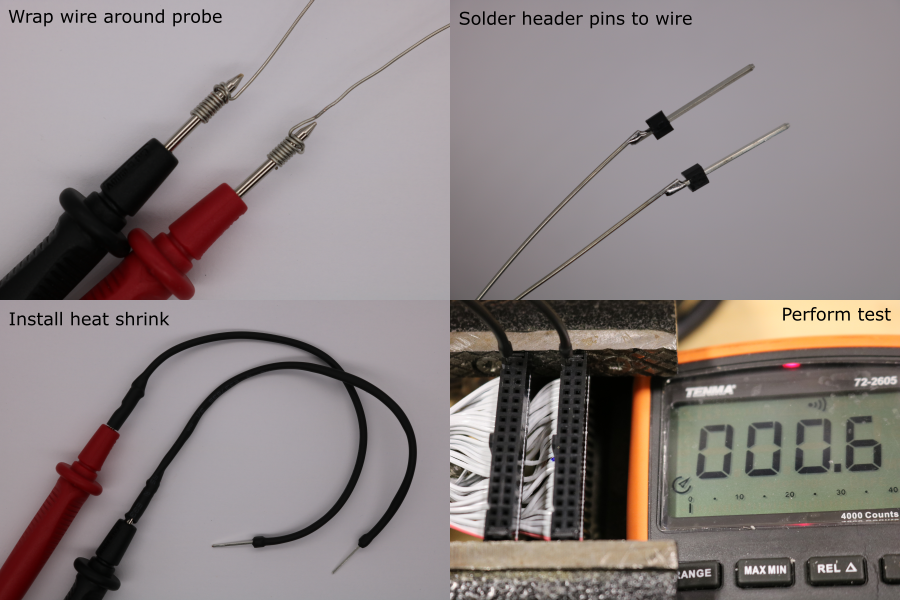
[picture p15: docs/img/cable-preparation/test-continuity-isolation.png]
test-continuity-isolation


1. Find a multimeter with probes that are compatible with the IDC socket.
1. If necessary, incompatible multimeter probes can be modified:
    * Cut 2 lengths of 120 mm solid core 28 awg wire.
    * Wrap one end tightly around each multimeter probe, using a knot.
    * Obtain two single header pins with 0.64 mm sqaure posts.
    * Solder each pin to the other end of the wire.
    * Cut a 120 mm length of heatshrink.
    * Install the heatshrink and shrink it onto the extended probe.
1. Hold the IDC connectors from each end of the cable in a vice. Make sure their orientation is the same.
1. Use the multimeter probes to test continuity and isolation according to the pattern shown in diagram below.
    * For continuous measurements the DC resistance should be \( < 1 \Omega \).
    * For isolated measurements the DC resistance should be out-of-range.

IDC-testing-pinout-diagram

## Sheath Surface Treatment for Bonding (Transducer End)

During the coating process, an adhesive bond to the PVC cable sheath is required. It is difficult to bond to PVC, so an abrasive surface treatment is used to increase bond strength.

1. Choose the end of the cable with the longest copper braid. This will be the transducer end of the cable.
1. Pull the copper braid back over the IDC connector.
1. Make a mark 36 mm from the end of the sheath using a permenant marker. Extend the mark around the sheath circumference.
1. Use a 24 tpi hacksaw blade (or similar) to abrade the cable sheath. The shiny PVC surface should be completely removed. Surface treatment should be applied up to at least 10 mm from the end of the sheath.
1. Pull the copper braid back over the sheath.
1. Wrap the end of the sheath in electrical insulating tape. The tape width should be \(\leq \) 14 mm.

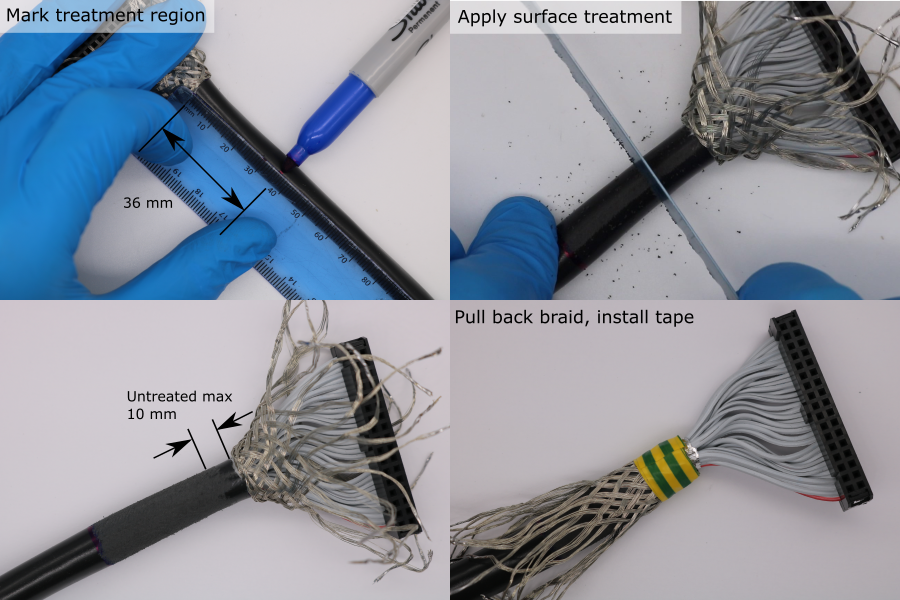
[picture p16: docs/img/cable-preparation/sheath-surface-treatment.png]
sheath-surface-treatment


## Copper Collar for Shield Termination (Plug End)

1. Cut a rectangle of adhesive-backed copper foil using scissors. The final ength of the copper collar should be 30 mm.
1. Wrap the copper foil around the sheath at the plug end of the cable, and rub the seam.
1. Setup a soldering iron with a temperature of 380 °C and a large-area tip.
1. Apply solder to the copper foil seam.
1. Use tweezers to untangle the copper braid.
1. Form 4 twisted bundles of copper braid, equally spaced around the cable circumference.
1. Bend one of the bundles so that its base touches the copper foil.
1. Pre-solder the base of a bundle.
1. Cut the bundle so that it overlaps the copper foil by ~4 mm.
1. Solder the trimmed bundle to the copper foil. Keep heating time to a minimum to avoid melting the PVC cable sheath.
1. Repeat this process for all four bundles.

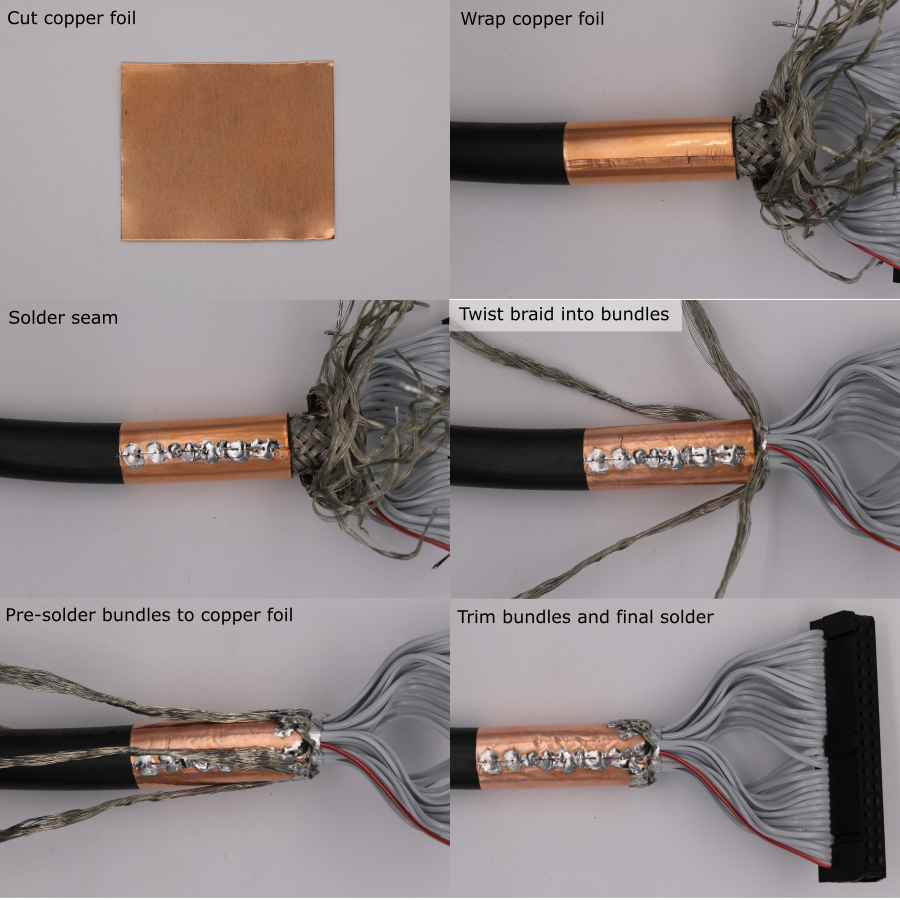
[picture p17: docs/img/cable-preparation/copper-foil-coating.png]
copper-foil-coating


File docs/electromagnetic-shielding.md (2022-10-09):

# Electromagnetic Shielding

## Install copper foil

1. Cut x3 50 mm strips of insulating polyamide tape.
1. Cover the exposed transducer PCB with the tape overlapping.
1. Manufacture the copper foil template pieces (further details [here](custom-tooling-manufacture.md)).
1. Trace the outline of the template pieces on a piece of adhesive-backed copper foil.
1. Cut out the copper foil pattern using scissors.
1. Place the transducer module on the larger copper foil pattern, with the PCB facing up.
1. Wrap the side tabs around the transducer module.
1. Place the smaller copper foil pattern on the PCB side of the transducer module.
1. Rub the copper foil all over with a hard stick so that the adhesive creates tight seams. 

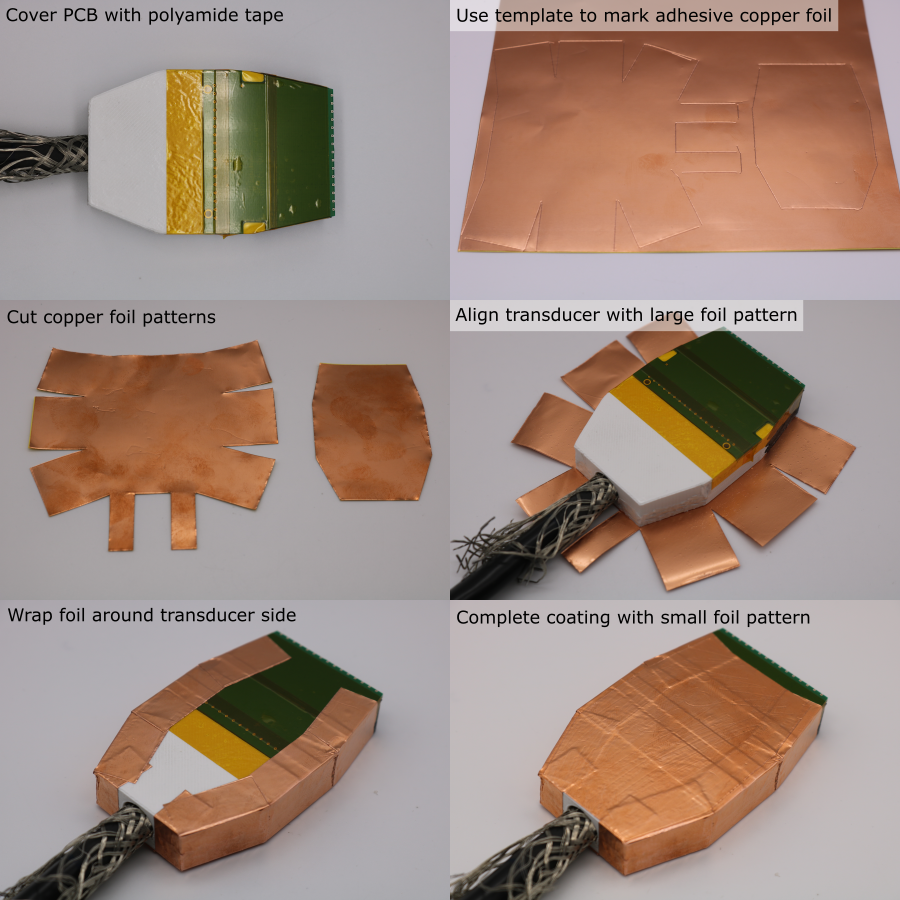
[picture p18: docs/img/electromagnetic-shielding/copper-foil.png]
copper-foil


## Bond Cable Braid to Transducer Shield

1. Use tweezers to untangle the copper braid.
1. Form 4 twisted bundles of copper braid, equally spaced around the cable circumference.
1. Bend one of the bundles so that its base touches the copper foil.
1. Pre-solder the base of the bundle.
1. Cut the bundle so that it overlaps the copper foil by ~4 mm.
1. Solder the trimmed bundle to the copper foil. Keep heating time to a minimum to avoid melting the transducer housing.
1. Repeat this process for all four bundles.
1. Use a scalpel to cutout x4 hexagons, exposing the mounting nut recesses.

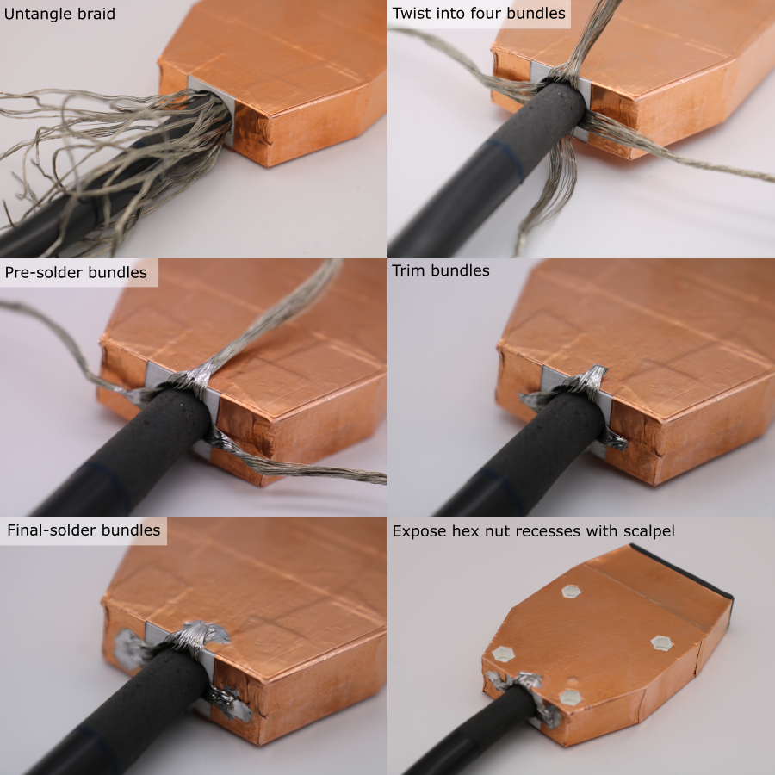
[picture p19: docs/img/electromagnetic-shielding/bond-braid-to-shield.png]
bond-braid-to-shield


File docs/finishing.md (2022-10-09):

# Finishing

## Dissolve Moulds

1. Remove the transducer module from the coating strong-plate.
1. Remove all of the screws from the coating moulds.
1. Place place the transducer-mould assembly in a bath of room temperature water for ~36 hours.
1. Pull away the silicone sealant from the cable.
1. After dissolving the mould, rinse in clean water and pat dry with a paper towel.

**Note:** Do not use warm water or agressive agitation since this can warp the internal plastic parts and damage the adhesive bond between the thin polyurethane coating and the transducer.

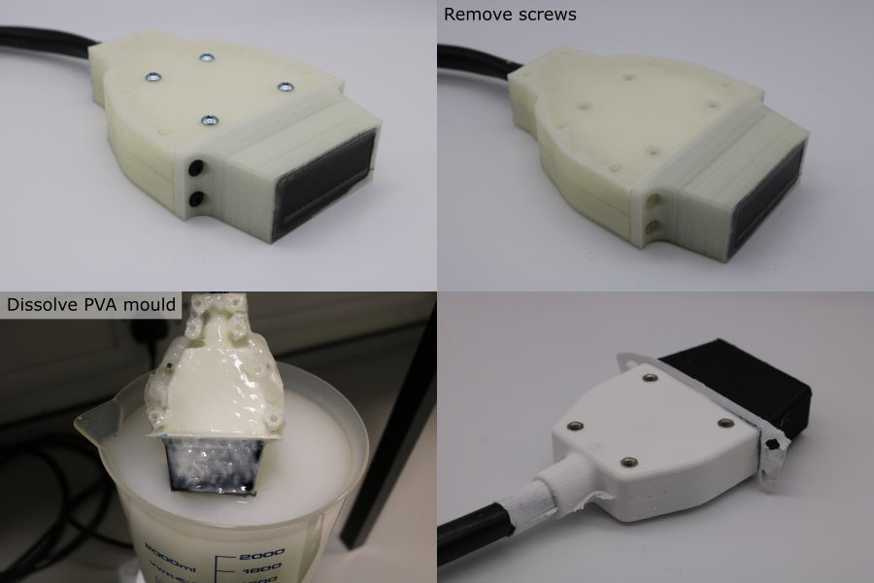
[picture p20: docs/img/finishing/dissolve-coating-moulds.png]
dissolve-coating-moulds


## Bend Relief Installation

1. Use a scalpel to remove the thin flashing created by the coating mould seams.
1. Cut a 32 mm piece of heatshrink using a pair of scissors.
1. Thread the heatshrink over the cable.
1. Pull the heatshrink over the collar where the cable enters the transducer module.
1. Hold the cable so that it is straight as it enters the transducer.
1. Use a heatgun to gently heat the sleeve, starting from the collar end. Heat from all directions, and allow the transducer to cool if the coating becomes too hot to touch.
1. Allow the heatshrink to cool fully before bending the cable.
1. The transducer module is now finished.

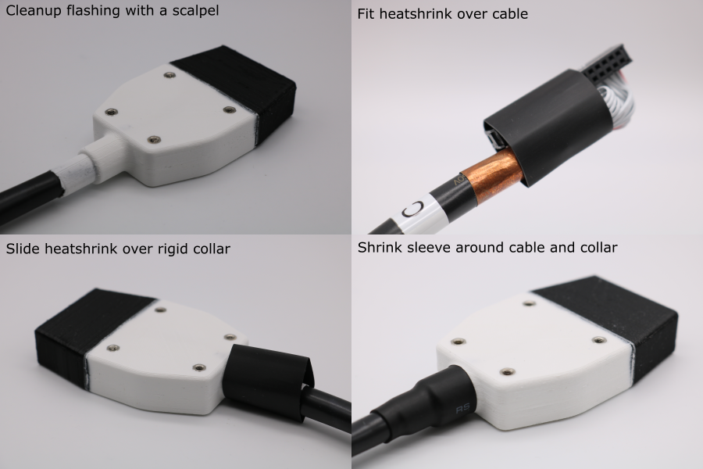
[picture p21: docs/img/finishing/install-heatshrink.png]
install-heatshrink


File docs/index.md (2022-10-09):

# open-UST

This is the documentation for the [open-UST](https://github.com/morganjroberts/open-UST) hardware distribution: an open source manufacturing framework for a low-cost, modular Ultrasound Tomography (UST) research system.

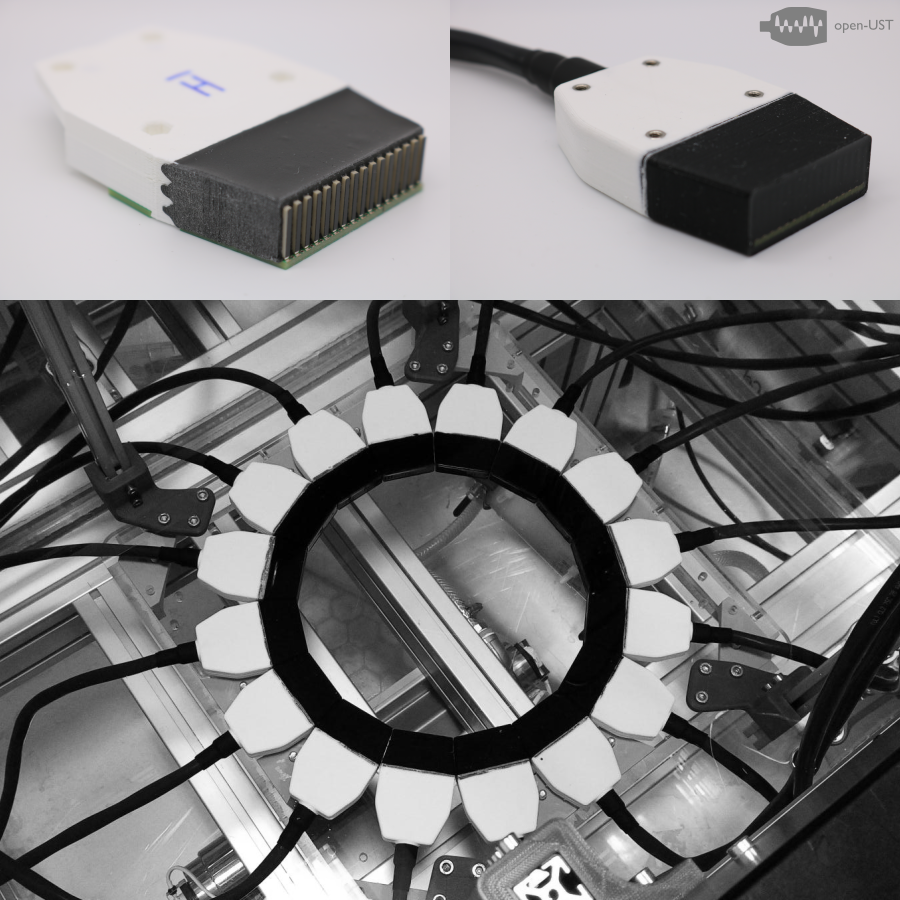
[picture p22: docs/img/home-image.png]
home-image


This documentation, and the hardware github repository, are continuously being expanded. Check back for further updates.

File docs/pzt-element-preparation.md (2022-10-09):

# PZT Element Preparation 

The PZT elements each have slightly different widths and thicknesses, due to deviations from the nominal values given on the datasheet (tolerances provided by the manufacturer for these PZT elements were \(\pm\) 130 \(\mu m\) for width and \(\pm\) 25 \(\mu m\) for thickness, detailed in: [`Piezoelectric Element Tolerances - APC International.pdf`](https://github.com/morganjroberts/open-UST/blob/main/hardware-distribution/technical-datasheets/Piezoelectric%20Element%20Tolerances%20-%20APC%20International.pdf)).

It is useful to measure these dimensions:

* The element widths are needed for calibrating the slot widths in the matching layer deposition mould, and the PZT alignment mould.
* If the unmatched and matched PZT element thicknesses are measured, these can be used to estimate the matching layer thicknesses (this data can be useful for quality control and when interpretting inter-element variations in acoustic performance).

## Load the PZT Element Tray

To store and keep track of the PZT elements, a gridded tray has been designed. This is accompanied by spreadsheet [`pzt-element-dimensions-defects.xlsx`](https://github.com/morganjroberts/open-UST/blob/main/hardware-distribution/pzt-element-dimensions-defects.xlsx), where the data rows and columns correspond to the physical row and column locations on the PZT element tray. Each PZT element should be assigned a PZT ID matching its row/column location in the storage tray e.g. 'A/3'.

PZT-element-tray

1. Manufacture the PZT storage tray (further details [here](custom-tooling-manufacture.md)).
1. Load the tray with PZT elements, using plastic tweezers.
1. Use M3 x 12 mm screws to secure the lid to the tray for storage.

## Dress the PZT Electrode Edges

* During manufacture the individual PZT bars are cut from a large slab. Sometimes the silver electrodes are not cut neatly to the edge of the PZT.
* The excess PZT electrode material can fold over onto itself during shipping and handling.
* The excess electrode can affect the thickness measurement of the PZT elements and can prevent the PZT elements from seating properly on the bottom face of the slots in the PVA mould during matching layer deposition.
* To fix this, the electrode edges should be "dressed" by scraping away the excess electrode material.

For each PZT element:  

1. Remove the PZT element from the tray using tweezers.
1. Hold the PZT element on a flat clean surface, under a microscope, with the electrode facing upwards.
1. Use a scalpel blade to gently chamfer the edges of the electrodes. Do not apply excessive downwards pressure with the scalpel. Do not touch the face of the electrode with the scalpel.

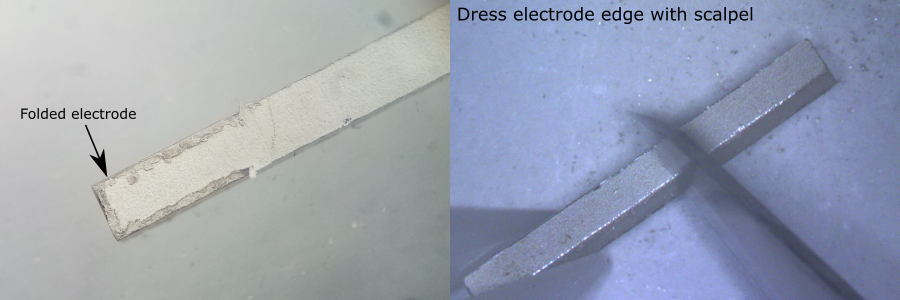
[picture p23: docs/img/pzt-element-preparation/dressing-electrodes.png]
dressing-electrodes


## Meaure the PZT Element Dimensions

1. Setup a micrometer securely in a clamp on a workbench.
1. Clean the micrometer anvils using a foam swab and isopropyl alcohol.
1. If using a digital micrometer, calibrate/tare it to 0.
1. Remove a PZT element from the storage tray with tweezers and clean using a foam swab and isopropyl alcohol.
1. Align the PZT element so that the electroded faces are parallel with the micrometer anvils.
1. Turn the ratcheting (rear-most) micrometer screw until it clicks.
1. Record the PZT element thickness.
1. Rotate the element so that the non-electroded faces are parallel with the micrometer anvils.
1. Record the PZT element width.
1. Gently drop the PZT element into the correct location in the PZT element tray, being careful not to scrape the PZT element against the hole wall.
1. Repeat for all PZT elements.

**Note:** Re-clean the micrometer anvils using a foam swab and isopropyl alcohol every 10 PZT elements.

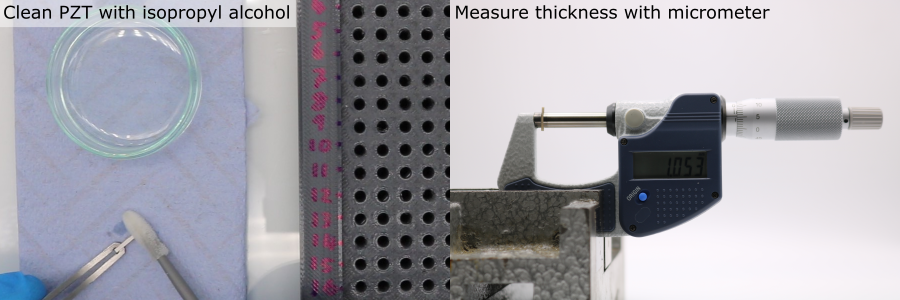
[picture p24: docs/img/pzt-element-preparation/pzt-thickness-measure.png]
pzt-thickness-measure


## Example Data

Width and thickness distributions were measured from the pool of PZT elements (N = 288) used for this project, using the procedure detailed above. Excess electrode folding was found to produce a systematic error in thickness measurement. A mean decrease of 22 \( \mu m \) was measured before and after dressing the electrode edges. The difference in standard deviation was negligible after dressing. In this case, the mean values for thickness and width match the nominal value provided by the manufacturer.

| Dimension                  | Mean [\( \mu m \)] | Standard Deviation [\( \mu m \)] |
| ---                        |    ----            |          ---                     |
| Thickness (Pre-dressing)   | 1021               | 8.2                              |
| Thickness (Post-dressing)  | 999                | 8.4                              |
| Width                      | 1000               | 20.4                             |

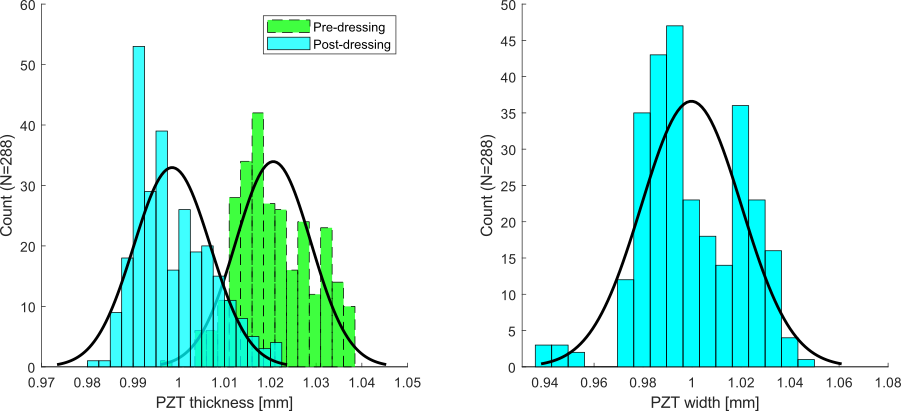
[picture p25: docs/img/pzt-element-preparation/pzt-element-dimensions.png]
pzt-element-dimensions


## Element Assignment

Make a list of PZT element IDs, ordered by their width. Matching layer deposition and PZT element alignment will be performed in batches. Within each batch, it is important that the PZT element widths are approximately equal.

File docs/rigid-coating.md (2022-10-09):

# Rigid Coating

## Seal Cable-Transducer Entry Point

1. Mount the transducer in the custom vertical clamp (further details [here](custom-tooling-manufacture.md)), taking care not to damage the PZT elements during handling.
1. Hold the cable in place vertically.
1. Clean the cable entry point and surrounding copper foil and braid using isopropyl alcohol and a foam swab.
1. Allow the solvent to evaporate.
1. Dispense equal parts (by volume) of Loctite EA9455 toughened epoxy onto a sacrificial piece of masking tape (~2 ml total).
1. Mix thoroughly for 1 minute using a small plastic rod, making sure all material is fully incorporated.
1. Use a foam swab to apply the epoxy to the cable entry point, forming a smooth fillet around the circumference. Make sure the joint completely covers the seam between the copper foil and the exposed housing region, to prevent leakage.

seal-cable-entry-point

## Prepare Coating Moulds

1. 3D-print the coating mould parts (orientation and slicer settings detailed in [3D-print-spec.pdf](https://github.com/morganjroberts/open-UST/blob/main/hardware-distribution/3D-print-spec.pdf)).
1. Allow the parts to cool for 1 hour.
1. If the parts are not being used immediately, store them in a sealed container to prevent dimensional changes due to humdity.
1. Cleanup nozzle stringing using a scalpel, and use an air duster to blow debris out of the parts.
1. Install M3 threaded inserts into the rigid coating split mould, using a soldering iron set to 275 °C. Make sure the top of the insert sits below the surface of the part to allow full contact between mating faces during assembly.
- Part A has x2 inserts
- Part B has x8 inserts
1. Use a scalpel to flatten any PVA squeezeout around the threaded inserts.
1. Use a paper towel to apply a layer of vaseline petroleum jelly to the threads of the M3 x 6 mm socket head bolts.

prepare-coating-moulds

## Assemble Coating Moulds

1. Degrease the sides of the transducer module using a paper towel soaked in isopropyl alcohol. Do not degrease the front face yet.
1. Use a fine paint brush to apply a bead of washable PVA glue onto the mating faces of each half of the rigid coating mould. 
1. Place the two halves of the mould either side of the transducer cable.
1. Install 6 M3 x 20 mm socket head screws through part A, into the threads in part B, to clamp the split mould together.
1. Use a foam swab to remove the PVA squeezeout inside the mould cavity, so that the internal mould seam is smooth.
1. Allow the PVA adhesive to dry for 1 hour.
1. Remove the M3 x 20 mm clamping screws from the mould.
1. Pull the transducer module through the mould so that the mounting nuts are aligned with the corresponding holes in part A.
1. Install the greased M3 x 6 mm socket screws to attach the transducer module to the mould. Tighten the screws so that there is no epoxy leakage during coating.
1. Dispense silicone sealant onto a sacrificial paper towel.
1. Use a foam swab to plug all of the holes in the coating mould with silicone sealant.
1. Use a gloved finger to seal the cable entry point to the mould with silicone sealant. A thick layer is needed since the PVC-silicone bond is weak. A thin coat could easily peel away when the transducer is handled.
1. Allow the silicone sealant to cure for 4 hours.

assemble-coating-moulds

## Fix Coating Mould to Strongplate

1. Manufacture the coating mould strongplate (further details [here](custom-tooling-manufacture.md)).
1. Install M3 screws through the strongplate and into the coating mould-transducer assembly (part A should be facing the strongplate).
1. Tighten the screws so that part A is pulled flat against the strongplate.
1. Install the acoustic coating mould using M3 x 8 mm screws.
1. Use a safety blade to test the transducer-mould alignment. The PCB should be level with the top surface of the acoustic coating mould.
1. Remove the acoustic coating mould.
1. If the PCB was too low, reduce the height of the acoustic coating mould by lapping it on a sheet of P180 grit abrasive paper.

assemble-coating-mould-strongplate

## Cast Rigid Coating

- **Note:** the working time of Glass Cast 10 is \(\geq \) 45 minutes, which is long enough that it this is not a limiting factor for the number of transducer modules that can be coated in one batch.
- **Note:** Be careful not to touch the front face of the transducer with the epoxy. If this happens, remove it immediately and rinse thoroughly with isopropyl alcohol.
- **Note:** The pigment is for cosmetic purposes only. Omitting it will not affect the curing properties of the epoxy.

Cast the coating using the following procedure:

1. Use an air duster to remove debris from the front face of the transducer module.
1. Use a foam swab and isopropyl alcohol to degrease the front face of the transducer module.
1. Test the fit of the 15ga blunt needle in the coating cavity.
1. If the needle is slightly too large, compress it in a vice until it fits.
1. Tightly push the needle luer-slip fitting onto the 60 ml syringe barrel and remove the plunger.
1. Calculate the required mass of resin, hardener and pigment. For four transducer modules, the required volume is 60 ml, and the required quantities are:

| Component | Mass [g] |
|-----------|----------|
|Resin |44.68|
|Hardener |20.11|
|Pigment |6.48|

1. Place a clean mixing pot on a digital balance (resolution 0.1 g or better), and tare it.
1. Dispense the required mass of resin.
1. Tare the balance.
1. Dispense the required mass of hardener.
1. Tare the balance.
1. Dispense the required mass of pigment.
1. Use a plastic rod to mix the components together for 5 minutes. Frequently scrape down the walls and bottom of the pot to make sure that all of the material is fully incorporated.
1. Pour the mixture into the syringe barrel.
1. Holding the syringe horiztonally, push the plunger into the syringe barrel until it forms a seal, but no further.
1. Gently rotate the syringe so that it is vertical, with the needle facing up, and allow the mixture to settle and for the air to rise to the top.
1. Slowly push the plunger to expell all of the air from the syringe.
1. Place the needle into the coating mould cavity, as far down as it will go (it may be necessary to wiggle the needle if the fit is tight).
1. Gently push the syringe plunger to dispense the epoxy into the mould.
1. Once the epoxy has reached the top of the mould, gently remove the needle from the mould.
1. Wait for 10 minutes to check that the epoxy is not internally into the transducer module, indicated by the level going down without visible external leaking (see note below).
1. Place the acoustic coating mould over the exposed transducer module.
1. Install 4 M3 x 8 mm screws to secure the acoustic coating mould to the rigid coating mould.
1. Allow to cure for 24 hours.

**Note:** If the epoxy is leaking internally, it will leak into the cable, making the cable rigid when the epoxy cures, which should be avoided. To stop a leak, use the needle and a new syringe to suck as much epoxy as possible out of the mould, wait for the epoxy to cure (this will seal the leak) and start the coating process again with a new batch of epoxy.

cast-rigid-coating

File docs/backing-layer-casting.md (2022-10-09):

# Backing Layer Casting

## Mould Masking

Masking tape is used to remove excess composite after casting.

1. Cut four pieces of masking tape for each transducer module.
1. Place these smoothly around the backing layer cavity.

masking-backing-cavity

## Prepare Tungsten-Epoxy composite

1. Calculate the required mass of tungsten, resin and hardener. For four transducer modules, the required volume is 42 ml. For a tungsten-weight fraction of 80.8 %, the required quantities are:

| Component | Mass [g] |
|-----------|----------|
|Tungsten powder |153.79|
|Araldite standard resin |20.30|
|Araldite standard hardener |16.24|

Use the Matlab function `tungstenPolymerRatio` to calculate the masses needed for other volumes and compositions.

1. Place a clean piece of paper on a digital balance (resolution 0.1 g or better), and tare it.
1. Dispense the required mass of tungsten powder, place aside for later.
1. Clean the glass mixing plate with isopropyl alcohol.
1. Place the glass plate on the digital balance, and tare it.
1. Dispense the required mass of resin.
1. Tare the balance.
1. Dispense the required mass of hardener.
1. Remove the glass plate from the balance and clamp securely to the work surface.
1. Use a flat scraper to combine the resin and hardener. Mix thoroughly for 5 minutes, making sure that all of the material is fully incorporated.
1. Add the tungsten powder.
1. Mix thoroughly for 15 minutes, making sure that the mixture is homogeneous. Frequently remove unmixed material from the scraper and the edges of the glass plate, using a safety blade, and combine it with the rest of the material.

tungsten-epoxy-mixing

## Composite Casting

1. Collect ~3 ml of composite on the end of the scraper.
1. First dispense the composite onto the wedged scattering structure on the front end of the transducer housing. Push the composite into the wedged cutouts so that they fill completely.
1. Next, slightly overfill the remaining backing layer cavity with composite. 
1. Remove the excess composite by sliding the scraper blade along the top surface of the housing and alignment mould. Do this in both directions, with the blade angled towards the direction of travel.
1. To fully remove the excess composite, carefully pull away the masking tape.
1. Allow the composite to cure for 24 hours.

backing-layer-casting

## Alignment Mould Removal

**Note:** Residual PVA can be gently removed from between the PZT elements using a toothbrush. Do not use warm water or agressive agitation since this can warp the housing, and damage the adhesive bond between the PZT and the matching and backing layers.

1. Remove the nylon screws that hold the module assembly to the base plate.
1. Transfer any module identification labels from the alignment mould to the housing using a permanent marker.
1. To dissolve the PVA alignment mould, place the module assembly in a bath of room temperature water for ~36 hours.
1. After dissolving the alignment mould, rinse in clean water and pat dry with a paper towel.
1. Once dry, use a scalpel to create a chamfer on the edges of the backing layer.

alignment-mould-removal

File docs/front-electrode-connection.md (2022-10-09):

# Front Electrode Connection

1. Use an air duster to remove and debris from the front electrode pads.
1. Prepare diluted conductive epoxy using the process described [earlier](rear-electrode-connection.md#conductive-epoxy-preparation).
2. Place the module assembly on the angled support plate, under a microscope.
3. Prepare a dispensing tool - attach a sewing needle to a long rod using tape.
4. Collect a drop of diluted conductive epoxy on the needle tip.
5. Place the drop on the PCB pad, and move the needle tip in small circles so that the drop touches the front electrode. The conductive epoxy should form a smooth fillet.
6. Repeat this process for all PZT elements in the transducer module.
7. Allow the conductive epoxy to cure for 24 hours.
8. Inspect the joints. Make sure that the conductive epoxy joints are flush with the edge of the PCB. If any of them overhang, use a new sharp scalpel blade to remove the excess material. 

front-electrode-connection

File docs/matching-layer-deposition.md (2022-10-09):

# Matching Layer Deposition

## Prepare PVA Deposition Mould

1. From the width ordered list of PZT elements, select a batch of 20 PZT elements with a similar width, and make a list of their PZT ID's.
1. Calibrate the slot width for the PVA deposition mould, (offset calibration process described [here](dimension-calibration-3D-printing.md#deposition-mould)).
1. 3D-print the PVA deposition mould for the current batch (orientation and slicer settings detailed in [3D-print-spec.pdf](https://github.com/morganjroberts/open-UST/blob/main/hardware-distribution/3D-print-spec.pdf)).
1. Allow the part to cool for 1 hour.
1. Carefully remove the part from the glass build plate using a scalpel.
1. Inspect the slots under a microscope. Remove any debris using a scalpel and an air duster.

prepare-deposition-mould

## Prepare Deposition Tooling

1. Manufacture the deposition tooling parts (further details [here](custom-tooling-manufacture.md)).
1. Remove debris from the deposition tooling parts using an air duster.
1. Degrease the deposition tooling parts using a paper towel/foam swab and isopropyl alcohol.
1. Use a foam swab to apply a coating of petroleum jelly to both sides of the steel gauge blocks, and to one side of each of the glass pieces.
1. Wipe off the coating using a paper towel to leave only a very thin layer that has negligible thickness.
1. Clamp the jig to the work surface using a small G-clamp.
1. Place the glass base into its recess, with the greased side facing up.
1. Install the coating rails and loosely install the M3 x 6 mm screws.
1. Place the PVA deposition mould onto the glass plate, in the same orientation that it was 3D-printed.
1. Install the retention clips and loosely install the M3 x 6 mm screws.
1. Adjust the parts so that there is no gap between the rails and the PVA deposition mould.
1. Tighten all the screws until the parts are fixed in place, but no further (to avoid flexing).
1. Place strips of masking tape on the glass plate beside the rails, and on the retention clips.

prepare-deposition-tooling

## Prepare and Load PZT elements

**Note:** PZT element electrodes are polarised, and come from the manufacturer with a polarity indicator (e.g. an ink marking). Polarity affects whether the PZT generates a positive or negative pressure wave when driven with a positive voltage pulse, and should be the same for all the elements in the array. Polarity errors can be identified during calibration, and corrected for with the driving voltage, but it is more convenient to make sure that the PZT elements are loaded into the deposition mould with the same polarity.

1. Identify the PZT element ID for the first deposition mould slot position, and remove the PZT element from the PZT storage tray using tweezers.
1. Find the side without a polarity indicator. This is the 'front electrode', and the composite will bond to this side.
1. Under a microscope, lightly abrade the surface of the front electrode using a small piece of P2000 grit sandpaper held in a pair of forceps. Do not remove excessive material.
1. Clean all faces of the PZT element using isopropyl alcohol and a foam swab.
1. Use tweezers to place the clean PZT element into the deposition mould slot, with the front electrode facing up. Make sure the PZT element is in full contact with the glass plate.
1. Repeat for all elements in the batch. Make sure that the location of each unique PZT ID within the deposition mould slots is recorded.

prepare-load-pzt

## Prepare Tungsten-Epoxy Composite

First calculate the required mass of tungsten, resin and hardener. For one batch of 20 PZT elements, the required volume is 5 ml. For a tungsten-weight fraction of 86.7 %, the required quantities are:

| Component | Mass [g] |
|-----------|----------|
|Tungsten powder |25.98|
|Araldite standard resin |2.18|
|Araldite standard hardener |1.74|

Use the Matlab function `tungstenPolymerRatio` to calculate the masses needed for other volumes and compositions.

1. Place a clean piece of paper on a digital balance (resolution 0.1 g or better), and tare it.
1. Dispense the required mass of tungsten powder, place aside for later.
1. Clean the glass mixing plate with isopropyl alcohol.
1. Place the glass plate on the digital balance, and tare it.
1. Dispense the required mass of resin.
1. Tare the balance.
1. Dispense the required mass of hardener.
1. Remove the glass plate from the balance and clamp securely to the work surface.
1. Use a flat scraper to combine the resin and hardener. Mix thoroughly for 5 minutes, making sure that all of the material is fully incorporated.
1. Add the tungsten powder.
1. Mix thoroughly for 15 minutes, making sure that the mixture is homogeneous. Frequently remove unmixed material from the scraper and the edges of the glass plate, using a safety blade, and combine it with the rest of the material.

prepare-composite

## Blade Coating Composite

**Note:** Only one coating stroke should be used. Practice this step first with an empty deposition mould to gain experience of how the composite behaves and how much is required.

1. Clean the custom blade coater using a foam swab and isopropyl alcohol.
1. Carefully place ~3 ml of composite above the first row of PZT elements, on the deposition mould. Do not allow the composite to touch the elements, as this can pull them up out of their slots.
1. Place the blade coater down onto the rails so that the composite is underneath the tool.
1. Slowly (~0.6 mm/s) drag the blade along the rails to coat the PZT elements with the composite. Make sure that even pressure is applied to the three points of contact between the blade coater and the rails/jig.
1. At the end of the coating stroke, slowly detach the blade from the composite using a side-to-side motion.
1. Remove the masking tape, being careful not to touch the coating layer.
1. Remove the rails, being careful not to touch the coating layer.
1. Use a paper towel and isopropyl alcohol to remove residue from the parts of the glass base previously covered by the rails and tape.

blade-coat-composite

## Composite Compression

1. Place the 2 clamp bases either side of the deposition mould.
1. Install the M3 x 12 mm screws and tighten until the clamps are fixed in place, but no further (to avoid flexing).
1. Use tweezers to place the steel gauge blocks in their recesses, either side of the deposition mould. Be very careful not to touch the coating layer.
1. Use tweezers to place one edge of the glass lid down so that it touches both gauge blocks. Once it touches the composite, do not lift it up.
1. Allow the glass to fall into place onto the gauge blocks. The greased side should be touching the composite.
1. Fix the clamp bars to the clamp bases using M3 x 6 mm screws.
1. Insert the M3 x 20 mm clamping screws into the clamp bar, and advance them so that they almost touch the glass lid.
1. In sequence, compress the composite layer. Tighten the four screws a quarter-turn at a time, to apply even clamping pressure. Stop once the glass lid touches the gauge block.
1. Label the glass lid with the batch ID using a permananent marker.
1. Allow the composite to cure undisturbed for 24 hours.

compress-composite

**Note:** During the manufacture of the transducers, there were major problems compressing the composite, due to the high viscosity of the composite. The high shear forces required were not achievable by clamping the glass plates, since they flexed and cracked. In future, thicker glass could be used, the clamping force could be spread over a larger area, and the blade coating thickness could be reduced. This custom tooling requires modification, which is an open issue on GitHub.

## Mould Removal

**Note:** Residual PVA can be gently removed from between the PZT elements using a toothbrush. Do not use warm water or agressive agitation since this can damage the adhesive bond between the PZT and the composite.

1. Dissasemble the coating tooling.
1. Use a scalpel to gently release the PVA deposition mould from the glass base. Do not attempt to remove the glass lid.
1. To dissolve the PVA deposition mould, place the glass-PZT-PVA assembly in a bath of room temperature water for ~36 hours.
1. Place the glass lid on a flat surface with the PZT elements facing up.
1. Use a scalpel to gently release the composite from the glass lid. Work slowly, from the outside inwards, from all directions.

deposition-mould-removal

## Matching Layer Trimming

**Note:** Change the scalpel blade for a new sharp one every 10 elements.

1. Place the composite-PZT assembly, with the rear electrodes facing up, on a flat surface under a microscope.
1. Use a scalpel to isolate a PZT element by cutting it out from the assembly.
1. Hold the PZT element down using plastic tweezers and use a scalpel to trim the composite flush with the edge on each side.
1. Repeat this to remove composite from the ends of the PZT element.
1. Rotate the PZT element so that the non-electroded side is facing up.
1. Hold the PZT with tweezers, and use a scalpel to shave the excess composite away from the PZT. The hard PZT can be used as a guide for the scalpel blade to run along, to cut the softer composite flush with the surface.
1. Repeat for the other non-electroded side of the PZT element.
1. Place the PZT element back in the PZT storage tray.
1. Repeat this process for all PZT elements.

matching-layer-trimming

## Matching Layer Thickness Measurement

1. Measure the matched-PZT thickness using the method described [earlier](pzt-element-preparation.md#meaure-the-pzt-element-dimensions).
1. Calculate the matching layer thickness for each element by subtracting the unmatched-PZT thickness from the matched-PZT thickness for each PZT ID.

## Expose the Front Electrode

1. Setup the custom matching layer trimmer by adjusting the blade and depth-stop to the correct position.
1. Remove a PZT element from the PZT storage tray using tweezers.
1. Place the PZT element, matching layer facing down, onto the custom trimming tool, with one of the ends touching the depth stop.
1. Use a soft push-stick (e.g. a pencil with eraser) to press the matching layer onto the blade.
1. If the matching layer did not separate fully, bring the PZT element under a microscope.
1. Use a scalpel blade to release the waste matching layer. Do not damage the electrode with the scalpel blade.
1. Record any defects (PZT chipping, electrode damage, matching layer damage), for the current PZT ID.
1. Return the PZT element to the PZT storage tray.
1. Repeat this process for all PZT elements.

expose-front-electrode

<!-- . Assess the PZT element for any defects. Possible defects are chipping (C), electrode delamination (E), sliced electrode (S), broken (B). Record these defects in spreadsheet [`pzt-element-dimensions-defects.xlsx`](https://github.com/morganjroberts/open-UST/blob/main/hardware-distribution/pzt-element-dimensions-defects.xlsx).
CHIPPING IMAGE PREVIOUSLY ON PREP PAGE -->

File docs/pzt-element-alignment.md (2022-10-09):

# PZT Element Alignment
<!-- Slot width affects orientation in lateral plane -->
<!-- elevation plane easier  -->

## Prepare Alignment Mould

1. From the width ordered list of PZT elements, select a batch of 20 PZT elements with a similar width, and make a list of their PZT ID's.
1. Calibrate the slot width for the PVA deposition mould (offset calibration process described [here](dimension-calibration-3D-printing.md#pzt-alignment-mould)). Adjust the required offsets in CAD and export the new stl file.
1. Print the stl file (orientation and slicer settings detailed in [3D-print-spec.pdf](https://github.com/morganjroberts/open-UST/blob/main/hardware-distribution/3D-print-spec.pdf)).
1. Label the part, marking the first (1) and last (16) element positions.
1. Allow the part to cool for 1 hour.
1. If the part is not being used immediately, store it in a sealed container to prevent dimensional changes due to humdity.
1. Cleanup nozzle stringing using a scalpel.
1. Use an air duster to blow debris out of the slots.

alignment-mould-preparation

## Prepare and Load PZT Elements

1. Orient the alignment mould with the blind end of the slots on the left and the PCB recess on the right.
1. Identify the PZT element ID for the first position, and remove the PZT element from the PZT tray using tweezers,
1. Under a microscope, lightly abrade the surface of the rear electrode using a small piece of P2000 grit sandpaper held in a pair of forceps. Do not remove excessive material.
1. Clean all faces of the PZT element using isopropyl alcohol and a foam swab.
1. Place the element on a clean surface and allow the solvent to evaporate.
1. Using a fine brush, paint the bottom of the alignment mould slot with washable PVA adhesive. Apply a thin coat, avoiding the side walls (excess PVA could squeeze onto the rear electrode, preventing bonding to the backing layer).
1. Wash the brush in water.
1. Using plastic tweezers, slide the clean PZT element into the slot, with the matching layer facing down, and the exposed front electrode on the right hand side, above the PCB recess.
1. Apply gently pressure with the tweezers to fully seat the element onto the bottom of the slot. Make sure the element is pushed fully into the blind end of the slot.
1. Repeat this process for all elements in the transducer module.

prepare-load-pzt-alignment-slots

## Apply PVA Blocking Layer

A PVA blocking layer is needed to prevent the backing layer composite from bonding to the exposed front electrode (this would later obstruct an electrical connection from the electrode to the PCB pad).

1. Under a microscope, apply a small drop of washable PVA adhesive to the end of the PZT element with a fine brush. Cover the gap between the alignment mould and the PZT element, where the matching layer has been removed to expose the front electrode. Do not cover the rear electrode.
1. Repeat this process for all elements in the transducer module.
1. Allow the adhesive to dry for 30 minutes.
1. Inspect the blocking layers. If the PVA adhesive does not completely block the gap next to the exposed electrode, apply a second blocking layer coat.

**Note:** if PVA adhesive is accidentally applied to the rear electrode, do not use solvent or water to remove it. Liquids can dissolve the surrounding PVA alignment mould and deposit a thin layer of PVA onto the rear electrode, preventing a proper bond between the electrode and the backing layer composite. Instead, allow the PVA adheisve to dry, then remove it using a small piece of P2000 grit sandpaper held in a pair of forceps. Remove the debris with an air duster.

pva-blocking-layer

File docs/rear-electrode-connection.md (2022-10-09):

# Rear Electrode Connection

## PZT-Housing Registration

1. Place the pre-loaded alignment mould onto the base plate, so that the interconnect PCB fits into the alignment mould PCB recess.
1. Install the M5 x 20 mm nylon screws, through the alignment mould, into the base plate.
1. Tighten the screws so that the alignment mould is clamped but can be re-positioned.
1. Under a microscope, perform the final alignment. The rear electrode of every PZT element must be directly above the front edge of its corresponding PCB pad.
1. Tighten the screws fully.
1. Inspect the final alignment under a microscope to check that the parts have not shifted when the screws were tightened.
1. Use an air duster to blow any debris out of the cavity.

pzt-housing-registration

## Conductive Epoxy Preparation

**Note:** Dilution with acetone has only been verified with MG chemicals 8331-14G. If using a different conductive epoxy, prepare a test sample to check the effect of acetone ratio on viscosity, and to verify that diluting with acetone does not affect the electrical and mechanical properties after curing.

1. Place a glass petri dish on a digital balance (resolution should be 0.01 g or better) and tare it.
1. Dispense 0.5 g of conductive epoxy part A.
1. Tare the balance.
1. Dispense 0.5 g of conductive epoxy part B.
1. Mix part A and part B with a small plastic rod (e.g. the handle of a foam swab).
1. Place the petri dish on the balance and tare it.
1. Using a pipette, dispense 0.1 g of acetone.
1. Incorporate the acetone.

conductive-epoxy-preparation

## Rear Electrode Connection

**Note:** The acetone evaporates from the mixture, increasing its viscosity. The effect of repeated dilution on the cured electrical properties of MG 8331-14G has not been tested. Instead, dispose of the mixture once it becomes too viscous to use, and prepare a new batch. Typically, it lasts for 15 minutes, which is enough time for ~3 transducer modules.

1. Place the module assembly on the angled support plate, under a microscope.
2. Prepare a dispensing tool - attach a sewing needle to a long rod using tape.
3. Collect a drop of diluted conductive epoxy on the needle tip.
4. Place the drop on the PCB pad, and move the needle tip in small circles so that the drop touches the rear electrode. The conductive epoxy should form a smooth fillet.
5. Repeat this process for all PZT elements in the transducer module.

Allow the conductive epoxy to cure for 24 hours. Once the conductive epoxy has cured, use a multimeter to check continuity between the conductive epoxy fillet and the rear electrode. Fix any defective joints if necessary.

**Note:** If the conductive epoxy is accidentally placed on the alignment mould, remove it after curing with a scalpel. If it is accidentally placed on the rear electrode, wipe off as much as possible with a foam swab, and any cured residue with a small piece of P2000 grit sandpaper held in a pair of forceps. In both cases remove any debris with an air duster.  Do not use solvents at any point, since they can dissolve the PVA alignment mould and deposit a thin layer of PVA on the rear electrode, preventing proper bonding with the backing layer composite.

rear-electrode-connection

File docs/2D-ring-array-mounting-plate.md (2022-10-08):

# 2D Ring Array Mounting Plate

This page is a work-in-progress and will be updated soon. 
It will provide guidance for the manufacture of the 2D ring array mounting plate assembly, which is used to hold the transducer modules in a water tank, in known positions relative to one another.

mounting-plate-summary-image

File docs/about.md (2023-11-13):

# About

##  Ultrasound Tomography and Breast Cancer
- Breast cancer screening with mammograms reduces mortality, but false negatives can occur for people with high breast density, and over-diagnosis causes harm in healthy people.
- Ultrasound Tomography (UST) is an emerging but promising modality that produces images of the sound-speed and acoustic-absorption distributions in breast tissue. These properties are useful biomarkers for classifying healthy and abnormal tissue types.
- UST could perform better than mammography, since it generates 3D images instead of 2D images.
- UST is also non-ionising, requires no painful breast compression, and is cheaper than MRI.

## Challenges in UST
- Widespread clinical adoption requires shorter data acquisition and image reconstruction times, while maintaining accuracy.
- Work towards this goal means that new methods must be tested experimentally.
- There is a high barrier to entry for researchers starting UST experiments: UST hardware is not available off the shelf, and custom systems are expensive.

## open-UST
**The goal of the open-UST project is to lower the barrier to entry for experimental UST researchers.**
This research project is guided by three objectives:

1. High accessibility for end users.
1. Nominal acoustic behaviour that supports UST imaging research.
1. Low inter-element variation (IEV) in acoustic behaviour.

This work will support researchers to build their own UST systems in house, accelerating progress towards fast and accurate UST imaging.

This documentation is part of the open-source hardware distribution.

## Features

- **Simple equipment requirements:** No specialist equipment required, only a 3D-printer, vacuum chamber and standard workshop tooling.
- **Low material cost:** ~£2k (excluding DAQ hardware) for a 256-element system.
- **Modular:** Both 2D and 3D imaging setups can be configured. 
- **Low interelement variation**: Recent testing showed that the individual sensing elements have uniform acoustic behaviour.
- **Other:**
    - Fully waterproof
    - Electromagnetically shielded
    - Transducer modules feature threaded mounting points for repeatable positioning
    - Includes option for a modular interface with the ITT Cannon DL5-260P connector (compatible with Verasonics)

## Citing open-UST

Please cite this article if you use open-UST in your research:

```
@article{roberts2023open,
  title     = {open-UST: An Open-Source Ultrasound Tomography Transducer Array System},
  author    = {Roberts, Morgan and Martin, Eleanor and Brown, Michael D and Cox, Ben T and Treeby, Bradley E},
  journal   = {IEEE Transactions on Ultrasonics, Ferroelectrics, and Frequency Control},
  year      = {2023},
  publisher = {IEEE},
  doi       = {10.1109/TUFFC.2023.3280635}
}
```

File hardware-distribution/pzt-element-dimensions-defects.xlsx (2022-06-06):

Defects |  | C=chipped |  |  | E=electrode delamination |  |  |  |  | S=sliced electrode |  |  |  | B=broken
 | A | B | C | D | E | F | G | H | I | J | K | L | M | N | O | P | Q | R
1 | - | - | - | - | - | B | - | - | - | - | - | - | E | - | - | C | - | -
2 | - | - | - | - | - | C | - | - | - | - | - | E | - | - | - | - | - | -
3 | - | C | E | - | - | - | - | C | - | - | E | C | - | - | E | - | - | -
4 | - | - | - | - | - | - | - | - | - | E | - | - | E | - | - | - | - | -
5 | - | - | - | - | - | - | - | - | - | - | - | - | - | - | - | - | - | -
6 | - | - | - | - | - | - | - | - | - | - | - | - | - | - | - | E | - | -
7 | - | - | - | - | - | - | - | E | - | - | - | - | E | CE | - | E | - | -
8 | - | E | - | - | - | - | - | - | - | - | - | - | C | - | - | - | - | -
9 | - | - | S | E | - | - | - | - | - | - | - | - | - | - | - | - | -
10 | - | C | - | - | - | - | - | - | - | - | - | S | - | C | - | - | -
11 | - | B | - | - | - | - | - | S | B | - | - | - | - | - | - | - | -
12 | - | - | - | - | - | - | - | - | - | - | - | - | - | - | - | - | -
13 | - | - | - | - | - | - | E | E | S | - | - | - | - | - | - | - | -
14 | - | - | - | - | - | - | - | - | - | - | E | - | - | - | E | - | -
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

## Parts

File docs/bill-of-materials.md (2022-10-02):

# Bill of Materials

The bill of materials is available [here](bom_link).

Site items may not be possible to source for all end users. These requirements:

## Sourcing PZT

* Redundancy defects
* APC
* Part number

pzt-element

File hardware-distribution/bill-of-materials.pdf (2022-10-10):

## open-UST Bill of Materials v1

Off-the-shelf components for transducer modules:
Item | Quantity per standard module | Unit | Manufacturer | Mfr. Part Number | Supplier Link
34-Way Screened Round Ribbon Cable | 2.5 | m | 3M | 3659-3 | RS 120-9135 (https://uk.rs-online.com/web/p/round-ribbon-cable/1209135/)
PZT elements: Plate 10.00mm x 1.00mm x 1.00mm 850-material | 16 | ea | American Piezo Ceramics | 689 | American Piezo Ceramics (https://www.americanpiezo.com/piezo-sale/piezoelectric-ceramics.html)
34-Way IDC Connector Socket for Cable Mount, 2-Row | 2 | ea | Amphenol | T812134A100CEU | RS 832-3639 (https://uk.rs-online.com/web/p/idc-connectors/8323639/)
34-Way 2-Row Right Angle SMT Header | 2 | ea | Samtec | TSM-117-01-L-DH | Farnell RS 208-6460 Mouser (https://uk.farnell.com/samtec/tsm-117-01-l-dh/conn-header-34pos-2row-2-54mm/dp/3515074?st=tsm-117-01)
Brass Hex Standoff Female/Female, 6mm, M3 x M3 | 4 | ea | Wurth Elektronik | 970060354 | RS 184-2804 (https://uk.rs-online.com/web/p/standoffs/1842804)
M3 Brass Threaded Insert diameter 4mm Depth 4.78mm | 4 | ea | RS PRO | 278-534 | RS 278-534 (https://uk.rs-online.com/web/p/threaded-inserts/0278534/)
M3 x 6mm Hex Socket Button Screw | 12 | ea | RS PRO | 822-9098 | RS 822-9098 (https://uk.rs-online.com/web/p/socket-screws/8229098/)
M5 x 30 mm Nylon Screw (Cheese Head) | 4 | ea | RS PRO | 291-262 | RS 291-262 (https://uk.rs-online.com/web/p/machine-screws/0291262)
M5 x 20 mm Nylon Screw (Cheese Head) | 3 | ea | RS PRO | 527-757 | RS 527-757 (https://uk.rs-online.com/web/p/machine-screws/0527757)
Heat Shrink Tubing, Black 19mm Sleeve Dia. x 5m Length 2:1 Ratio | 30 | mm | RS PRO | 700-4664 | RS 700-4664 (https://uk.rs-online.com/web/p/heat-shrink-tubing/7004664)

Consumable materials for transducer modules:
Item | Quantity per standard module | Unit | Manufacturer | Mfr. Part Number | Supplier Link
Silver Conductive Adhesive Epoxy | 0.5 | g | MG Chemicals | 8331-14G | RS 918-5002 (https://uk.rs-online.com/web/p/adhesives/9185002/)
5 micron Tungsten Powder | 53 | g | Tungsten Alloys | - | Tungsten Alloys (http://www.tungsten-alloys.co.uk/)
Araldite Standard Epoxy Adhesive | 14 | ml | Araldite | ARA-400003 | RS 756-0114 (https://uk.rs-online.com/web/p/adhesives/7560114/)
AptFlex F7 Acoustic Encapsulation | 20 | ml | Precision Acoustics | APLF7NC | Precision Acoustics (https://www.acoustics.co.uk/product/aptflex-f7/)
Polyamide/Kapton Tape | 300 | mm | Tesa | 51408-00008-00 | RS 436-2778 (https://uk.rs-online.com/web/p/masking-tapes/4362778/)
Copper Foil 210mm L, 160mm W, 0.03mm Thickness | 1 | sheet | Sunhayato | T-160C | RS 634-8998 (https://uk.rs-online.com/web/p/metal-sheets/6348998/)
GlassCast 10 Clear Epoxy Casting Resin | 16 | ml | Easy Composites | EP-G10-1 | Easy Composites (https://www.easycomposites.co.uk/glasscast-10-clear-epoxy-casting-resin)
Super White CULR Epoxy Pigment | 2 | ml | Easy Composites | PG-CU-SW-002 | Easy Composites (https://www.easycomposites.co.uk/super-white-epoxy-pigment)
Loctite EA9455 | 2 | ml | Henkel | 451277 | RS 458-9513 (https://uk.rs-online.com/web/p/adhesives/4589513/)
Loctite 3090 2K Cyanoacrylate | 2 | g | Henkel | 3090 | Farnell (https://uk.farnell.com/loctite/3090-10g/adhesive-2-component-loctite-3090/dp/1835175?ost=loctite+3090)

Off-the-shelf components for DL5-260P plug assembly:
Item | Quantity for one plug (128 channel) | Unit | Manufacturer | Mfr. Part Number | Supplier Link
M3 x 30mm Hex Socket Cap Screw Black | 2 | ea | RS PRO | 467-9846 | RS 467-9846 (https://uk.rs-online.com/web/p/socket-screws/4679846/)
M3 x 10mm Hex Socket Button Screw | 18 | ea | RS PRO | 281-192 | RS 281-192 (https://uk.rs-online.com/web/p/socket-screws/0281192/)
AMPMODU 20 Way 2 Row Straight PCB Socket | 1 | ea | TE Connectivity | 1-215307-0 | RS 495-8701 (https://uk.rs-online.com/web/p/pcb-sockets/4958701)
AMPMODU 4 Way 2 Row Straight PCB Socket | 8 | ea | TE Connectivity | 215307-2 | Farnell (https://uk.farnell.com/amp-te-connectivity/215307-2/btb-connector-rcpt-4pos-2row-tht/dp/3398086?gross_price=true)
24 Way, 2 Row, straight pin header | 1 | ea | Wurth Elektronik | 61302421121 | RS 828-1547 Digikey (https://uk.rs-online.com/web/p/pcb-headers/8281547/)
8 Way, 2 Row, straight pin header | 1 | ea | Wurth Elektronik | 61300821121 | RS 828-1525 (https://uk.rs-online.com/web/p/pcb-headers/8281525/)
DL5-260PW6A Plug with square post pins | 1 | ea | ITT Cannon | DL5-260PW6A | Farnell (https://uk.farnell.com/itt-cannon/dl5-260pw6a/backplane-conn-plug-260pos-2-54mm/dp/3727171)
5650M zero-ohm link | 16 | ea | Yageo | RC2010JK-070RL | RS 198-8503 (https://uk.rs-online.com/web/p/surface-mount-fixed-resistors/1988503/)

Other Consumable Materials
Item | Manufacturer | Mfr. Part Number | Supplier Link
Acetone | RS PRO | 918-1082 | RS 918-1082 (https://uk.rs-online.com/web/p/electronics-cleaners/9181082/)
Isopropyl Alcohol | RS PRO | 227-4427 | RS 227-4427 (https://uk.rs-online.com/web/p/electronics-cleaners/2274427)
White PLA Filament 2.85mm | RS PRO | 832-0273 | RS 832-0273 (https://uk.rs-online.com/web/p/3d-printing-materials/8320273)
PVA-M Filament 2.85mm | Dutch Filaments | 246190101 | 3DFilaPrint (https://3dfilaprint.com/product/2-85mm-pva-m-500gms-by-dutch-filaments/)
Steel 0.2 mm shim stock | RS PRO | 518-879 | RS 518-879 (https://uk.rs-online.com/web/p/steel-shims/0518879)
10mm Acrylic Sheet | Any
Bathroom silicone sealant | Any
Electrical Tape | Any
Petroleum Jelly | Vaseline
Washable PVA adhesive | Rymans | 680155586 | Rymans (https://www.ryman.co.uk/ryman-pva-glue-washable-250ml-1)

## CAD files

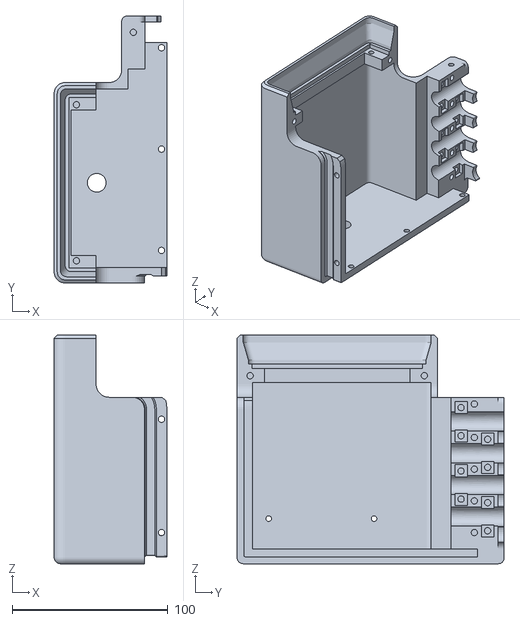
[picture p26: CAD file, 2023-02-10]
hardware-distribution/UTA-260-D-plug/UTA-260-D-plug-main-body.stl
72.3 x 171.2 x 146.5

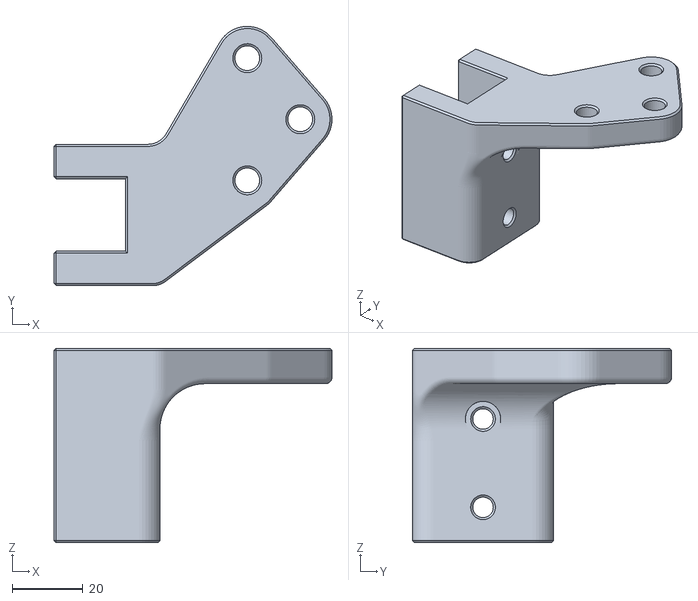
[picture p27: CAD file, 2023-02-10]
hardware-distribution/array-mounting-plate/sliding-bracket-left.stl
78.7 x 73.4 x 55.0

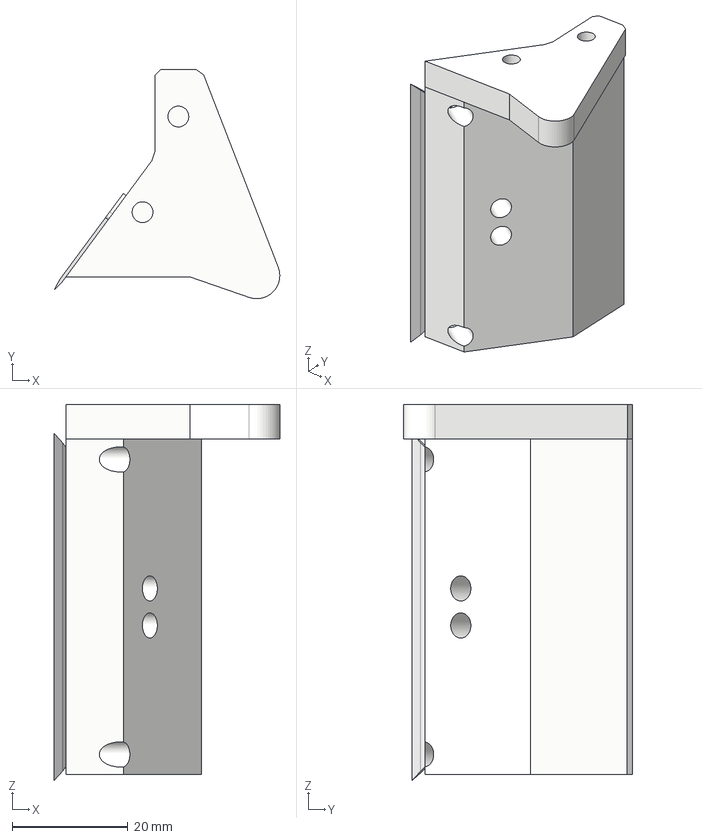
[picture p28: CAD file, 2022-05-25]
hardware-distribution/custom-tooling/doctor-blade-coater/doctor-blade-coater.step
39.0 x 39.6 x 65.0 mm
Blade
Blade Holder
Support Arm

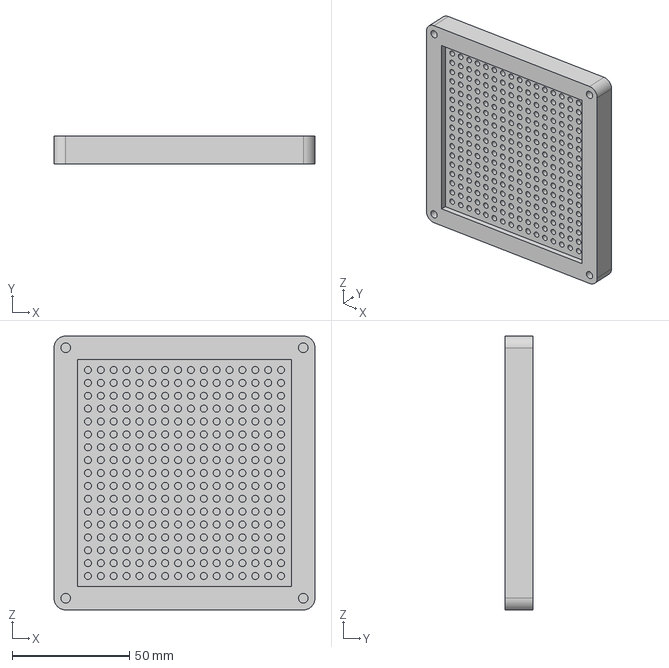
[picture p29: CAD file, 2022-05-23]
hardware-distribution/custom-tooling/pzt-element-tray/pzt-element-tray.step
111.5 x 12.0 x 117.0 mm

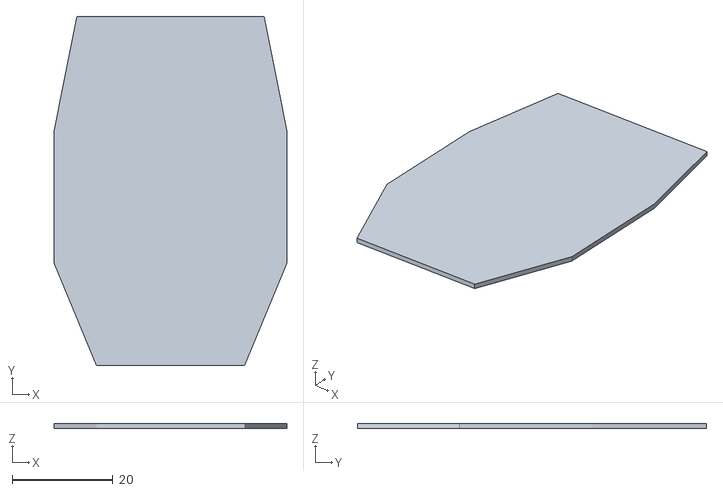
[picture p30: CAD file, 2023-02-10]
hardware-distribution/custom-tooling/shielding-template-2.stl
46.3 x 69.4 x 1.00

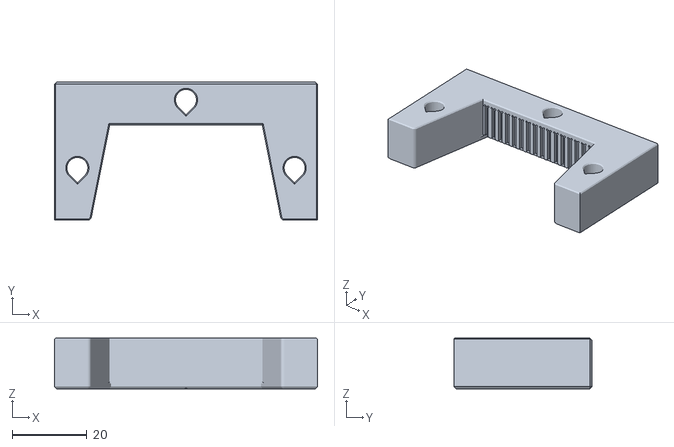
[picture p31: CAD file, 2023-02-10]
hardware-distribution/transducer-module/PZT-alignment-moulds/PZT Alignment Mould +0.118_sswo_0.55mm_corner_0.075mm_gap.stl
70.3 x 37.0 x 13.6

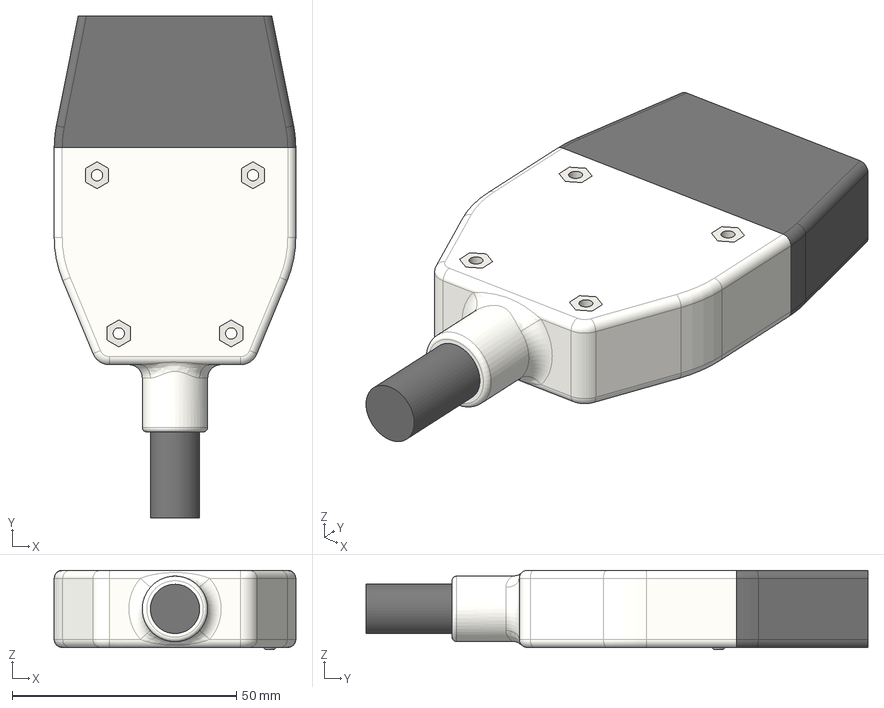
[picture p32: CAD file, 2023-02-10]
hardware-distribution/transducer-module/transducer-module.step
53.9 x 112.0 x 17.7 mm
PZT Elements
PCB
Backing Layer
SMT Header
IDC Connector
Housing
Ribbon Cable
Cover
Mounting Nuts
Acoustic Coating
Rigid Coating

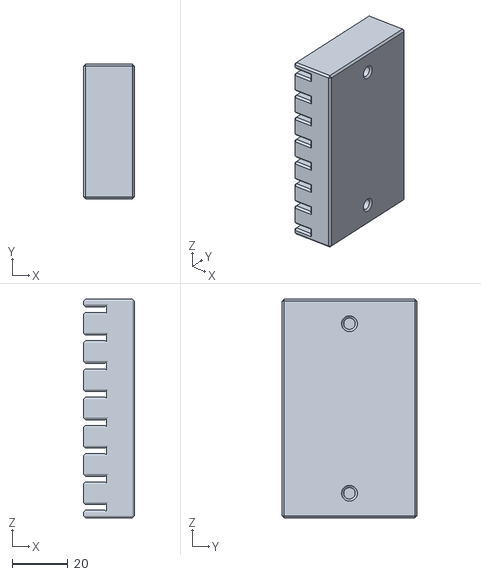
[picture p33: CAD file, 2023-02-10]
hardware-distribution/UTA-260-D-plug/UTA-260-D-plug-matching-pcb-spacer-block.stl
18.5 x 48.5 x 78.7

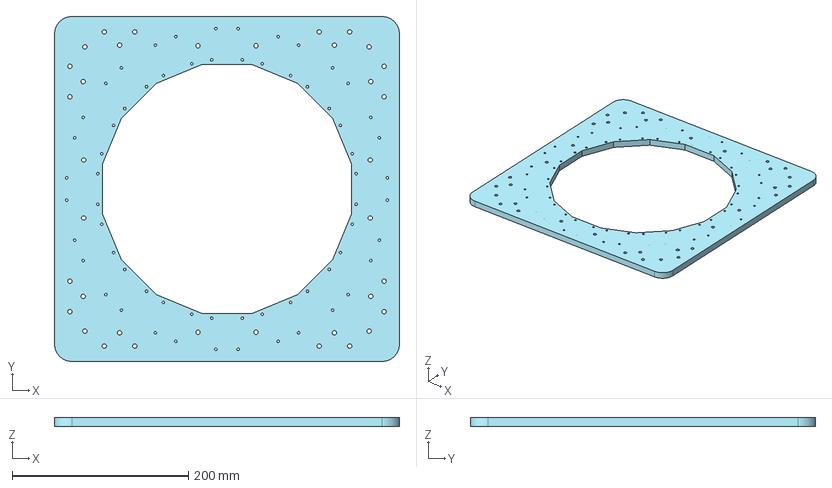
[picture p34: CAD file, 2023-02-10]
hardware-distribution/array-mounting-plate/array-mounting-plate.step
391.1 x 391.1 x 10.0 mm

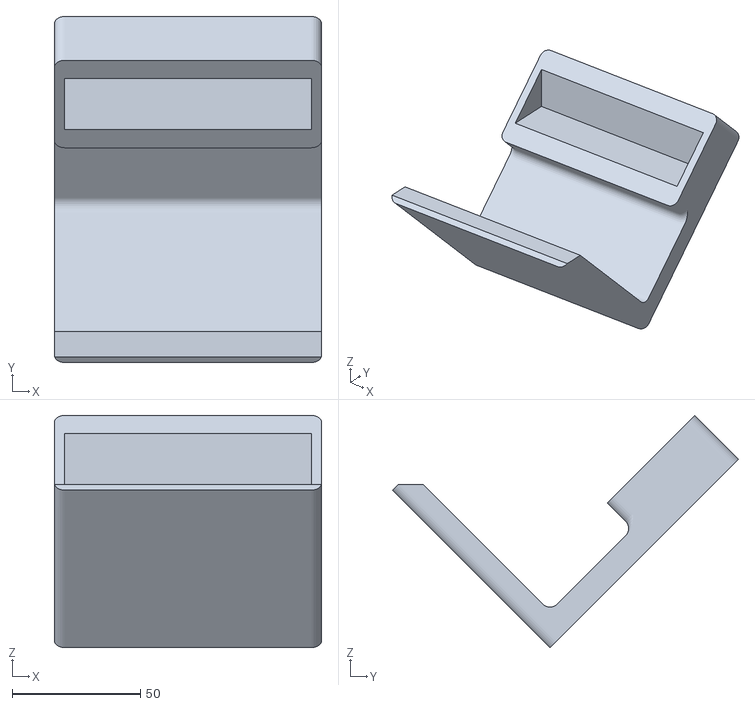
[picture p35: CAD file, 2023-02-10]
hardware-distribution/custom-tooling/inclined-jig.stl
104.3 x 135.0 x 90.6

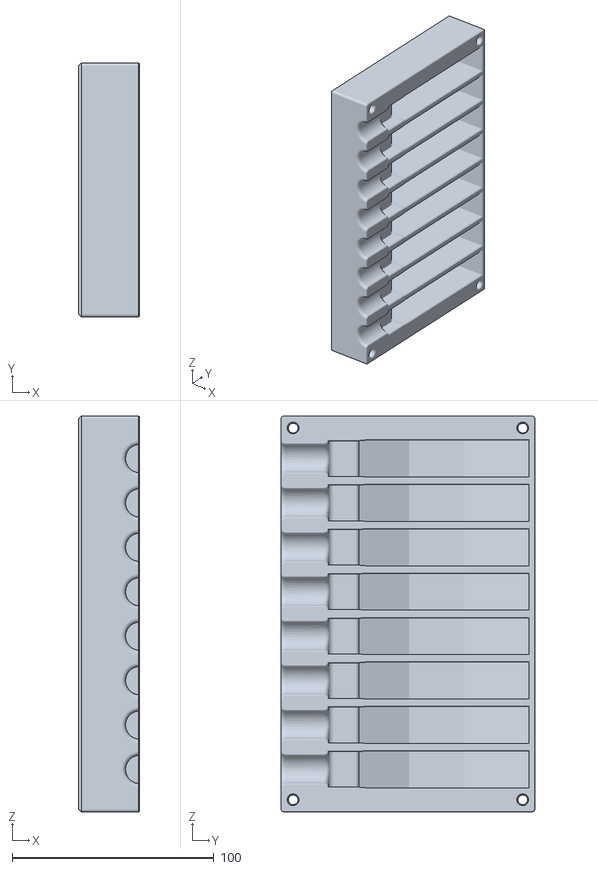
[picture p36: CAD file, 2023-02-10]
hardware-distribution/transducer-module/storage-box-lid.stl
30.5 x 125.8 x 196.2

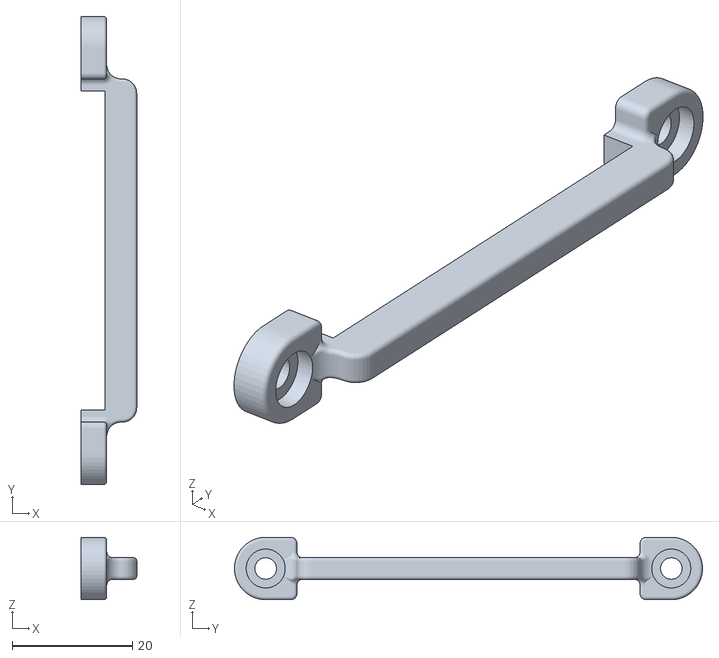
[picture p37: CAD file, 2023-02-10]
hardware-distribution/UTA-260-D-plug/UTA-260-D-plug-breakout-pcb-retention-bar.stl
9.25 x 77.9 x 10.4

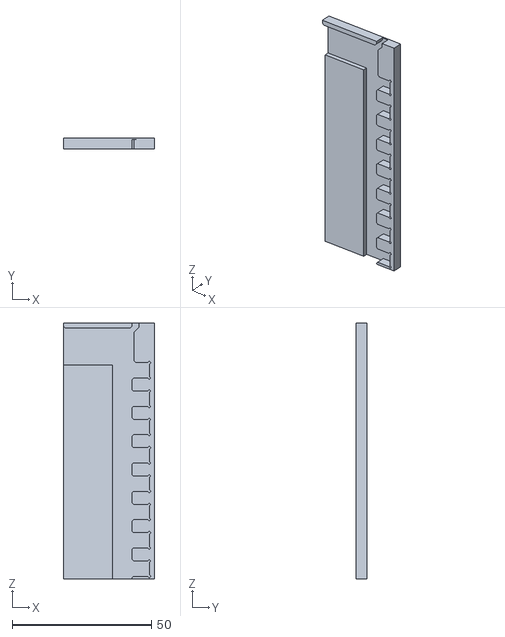
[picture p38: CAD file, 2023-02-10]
hardware-distribution/custom-tooling/breakout-pcb-soldering-jig.stl
32.5 x 3.83 x 91.8

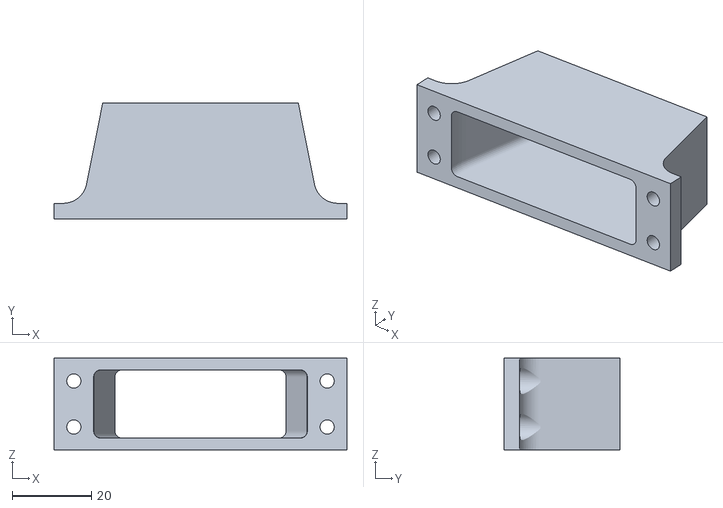
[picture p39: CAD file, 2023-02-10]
hardware-distribution/transducer-module/acoustic-coating-mould.stl
73.9 x 29.4 x 23.2

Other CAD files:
hardware-distribution/custom-tooling/pzt-element-tray/PZT Element Tray 16x17 10 mm length.stl
hardware-distribution/transducer-module/PZT-alignment-moulds/PZT Alignment Mould +0.1_sswo_0.55mm_corner_0.075mm_gap.stl
hardware-distribution/array-mounting-plate/sliding-bracket-right.stl
hardware-distribution/transducer-module/PZT-alignment-moulds/PZT Alignment Mould +0.106_sswo_0.55mm_corner_0.075mm_gap.stl
hardware-distribution/UTA-260-D-plug/UTA-260-D-plug-backshell.f3d
hardware-distribution/UTA-260-D-plug/UTA-260-D-plug-breakout-pcb-spacer-block.stl
hardware-distribution/UTA-260-D-plug/UTA-260-D-plug-clamp-bar.stl
hardware-distribution/UTA-260-D-plug/UTA-260-D-plug-coupler.stl
hardware-distribution/UTA-260-D-plug/UTA-260-D-plug-lever.stl
hardware-distribution/UTA-260-D-plug/UTA-260-D-plug-lid.stl
hardware-distribution/array-mounting-plate/array-mounting-plate.dxf
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

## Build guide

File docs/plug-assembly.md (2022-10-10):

# Plug Assembly

## Overview

## 3D-Print the Plug Parts

1. 3D-print the plug parts (orientation and slicer settings detailed in [3D-print-spec.pdf](https://github.com/morganjroberts/open-UST/blob/main/hardware-distribution/3D-print-spec.pdf)).
1. Remove the support material, using a room temperature water bath for parts with PVA support.

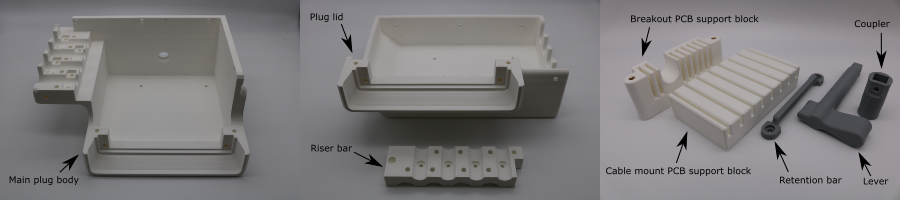
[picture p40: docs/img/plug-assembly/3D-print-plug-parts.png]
3D-print-plug-parts


## Copper Coating Backshell Parts

Coat the inner surfaces of the two halves of the split plug backshell, and the outside of the riser bar, using the following process:

1. Use calipers to take a dimension from the part.
1. Transfer these dimensions to a sheet of adhesive-backed copper foil.
1. Cut the required shape from the foil using scissors.
1. Remove the adhesive backing and stick the copper foil to the part. Overlap with previously applied pieces of copper. Push the foil all the way into corners using a hard object. Rub the seams to ensure good adhesion.
1. Repeat this until the parts are fully coated.
1. Use a scalpel to expose any covered holes.

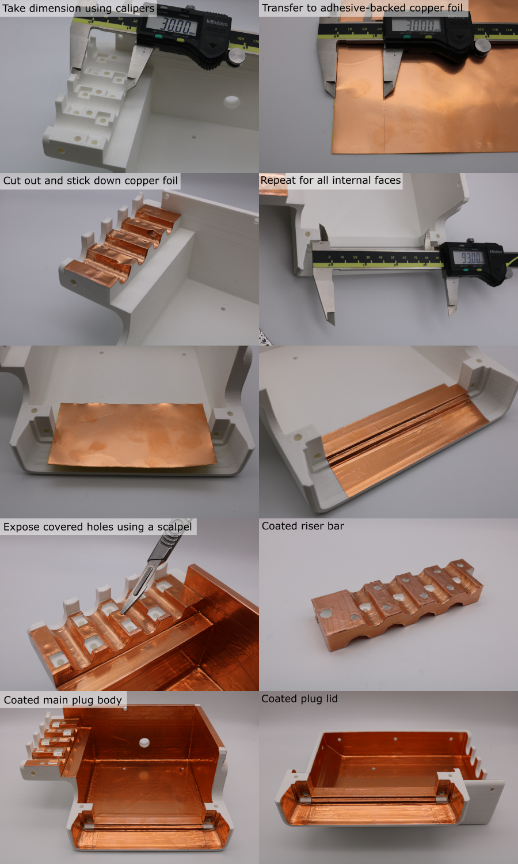
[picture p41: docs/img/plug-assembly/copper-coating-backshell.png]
copper-coating-backshell


## Finishing Backshell Parts

1. Setup a soldering iron with a temperature of 380 °C, with a large tip.
1. Apply solder joints to the seams between individual copper foil pieces to permenantly attach them. Space the joints every ~15 mm. Make sure that any loose flaps are tacked down with solder.
1. Setup a solering iron with a temperature of 275 °C, and a clean tip.
1. Use the soldering iron to install the threaded inserts so that they sit just below the surface of the part.

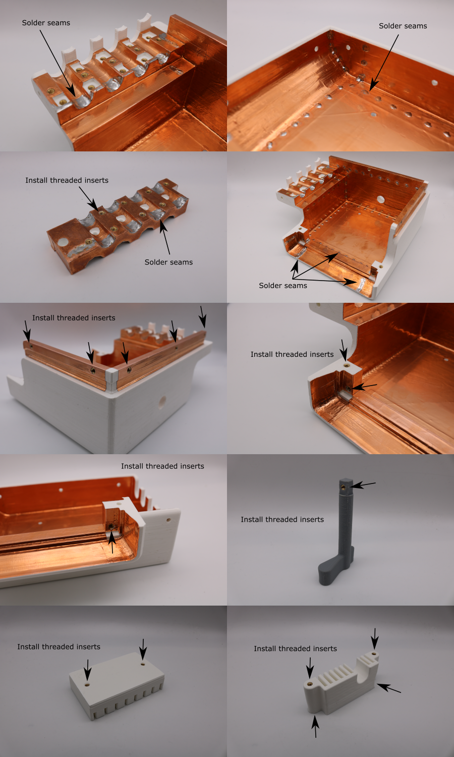
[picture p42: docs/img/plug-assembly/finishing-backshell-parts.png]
finishing-backshell-parts


## Solder the DL5 Breakout PCB

1. Setup a soldering iron with a temperature of 350 °C and a small tip.
1. 3D-print the breakout PCB soldering jig (further details [here](custom-tooling-manufacture.md)).
1. Load x8 of the AMPMODU 4-way sockets into the soldering jig.
1. Place the breakout PCB into the soldeing jig, aligning the socket legs with the pads. Make sure the egde of the PCB is pushed squarely against the base of every socket.
1. Solder the sockets to the PCB. Use small solder joints and short heating times to prevent shorting the signal and ground pins.
1. Attach x1 of the AMPMODU 10-way sockets to the end of the PCB, aligning the socket legs with the pads. Make sure the edge of the PCB is pushed squarely against the base of the socket.
1. Solder the socket in place.
1. Flip the PCB and solder the joints on the other side.

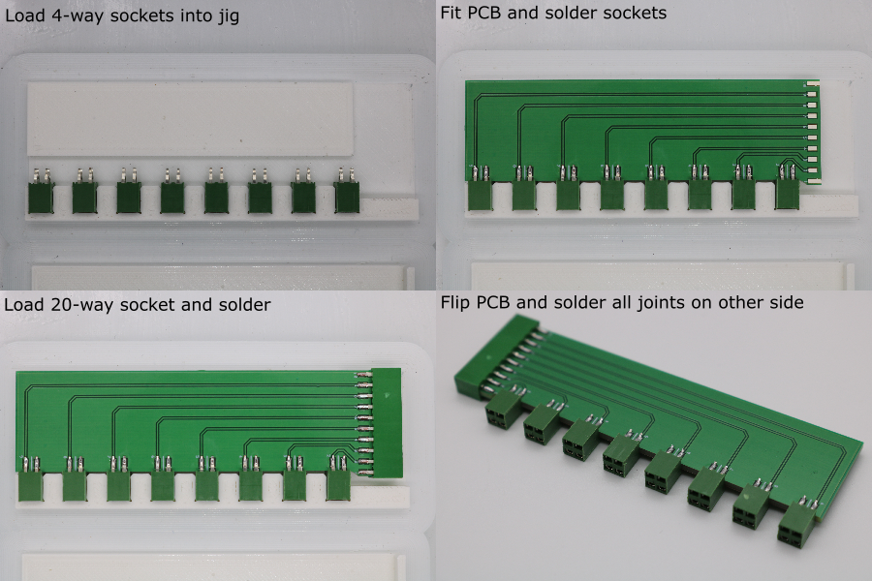
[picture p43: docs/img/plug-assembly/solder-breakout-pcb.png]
solder-breakout-pcb


## Solder the Cable Mount PCB

Note: If impedance matching is being used, the SMT component below refers to an inductor. If not, then the SMT component will be a zero-ohm link.

1. Setup a soldering iron with a temperature of 350 °C and a small tip.
1. 3D-print the cable mount PCB soldering jig (further details [here](custom-tooling-manufacture.md))
1. Load x1 8-way Wurth header pin strip and x1 24-way Wurth header pin strip into the soldering jig.
1. Place the cable mount PCB into the soldeing jig, aligning the socket legs with the header pins. Make sure the egde of the PCB is pushed squarely against the base of every header pin strip.
1. Solder the header pins to the PCB. 
1. Flip the PCB and solder the joints on the other side.
1. Position x1 Samtec header pin strip onto the PCB.
1. Solder the header pins to the PCB. 
1. To prepare for SMT component installation, apply a bead of solder to one pad for each of the SMT pad-pairs.
1. Use tweezers to position the SMT component above a pad-pair, and re-melt the solder to fix the component in place.
1. Solder the other end of the SMT component to its pad.

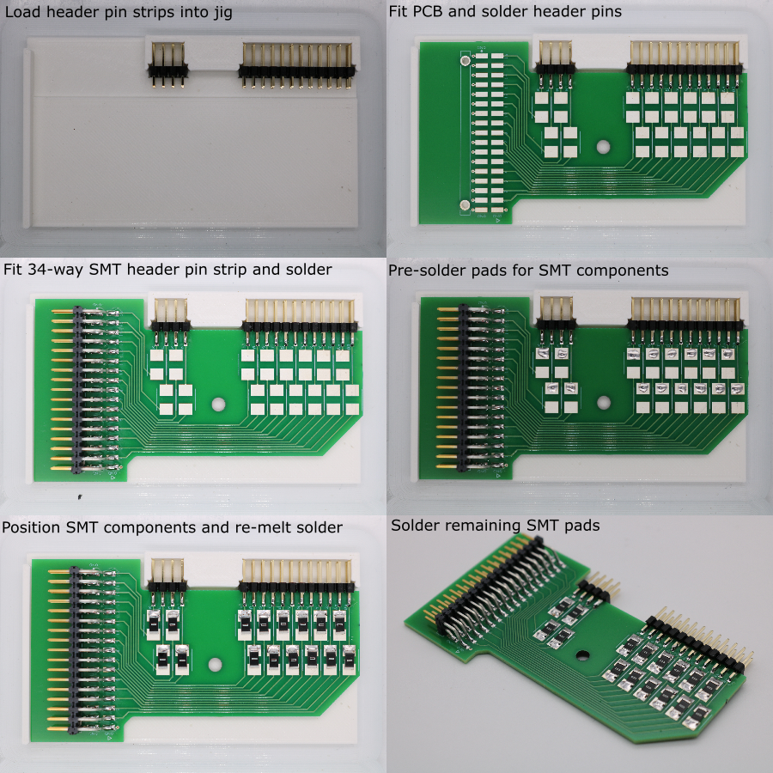
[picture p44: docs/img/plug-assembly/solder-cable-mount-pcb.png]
solder-cable-mount-pcb


## Assemble the Plug Components

1. Attach the breakout PCB support block to the main plug body using two M3 x 10 mm screws.
1. Attach the coupler to the shaft of the DL5-260P connector using an M4 x 12 mm screw.
1. Push the breakout PCBs onto the DL5-260P connector pins.
1. Attach the DL5-260P connector to the main plug body using two M3 x 10 mm screws. Pay attention to the plug polarity, shown in the picture below. The breakout PCBs should fit into the grooves in the support block.
1. Attach the retention bar to fix the breakout PCBs to the support block, using 2 M3 x 6 mm screws.
1. Push the lever through the hole in the main plug body, into the coupler. Make sure the hole in the coupler aligns with the threaded insert on the end of the lever.
1. Secure the lever to the coupler using an M3 x 6 mm screw.
1. Install a cable mount PCB on to the end of each transducer module. Make sure that the polarity indicator (embossed triangle on IDC / red wire) is on the same side as the triangle printed on the PCB. The tab on the IDC connector should be facing away from the PCB.
1. Push the header pins on cable mount PCB 'A' into the sockets on breakout PCB stack.
1. Position a strain relief clip over the copper foil cable collar, and attach fix the cable to the main plug body using two M3 x 6 mm screws. The screw heads must sit below the surface.
1. Repeat this for every other transducer modules  ('C', 'E', and 'G').
1. Install the riser bar on top of the cables, using five M3 x 10 mm screws.
1. Repeat the cable mount PCB installation process for the remaining transducer modules ('B', 'D', and 'F').
1. Install the jumper shorting the DL5 connector pins A1 and A2.
1. Positon the cable mount pcb support block.
1. Place the plug lid over the plug main body. 
1. Make sure the holes in the support block are aligned with the holes in the plug lid, adjusting if necessary.
1. Fix the plug lid to the support block using two M3 x 10 mm screws.
1. Fix the plug lid to the DL5-260P connector using two M3 x 10 mm screws.
1. Fix the plug lid to the plug main body connector using six M3 x 10 mm screws, and two M3 x 30 mm screws.

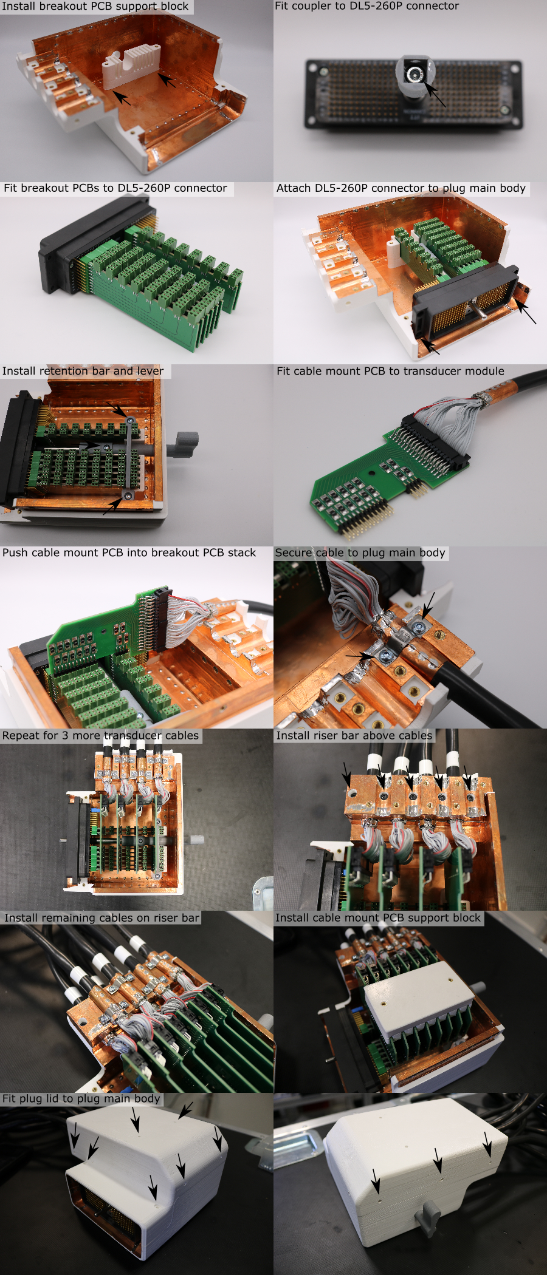
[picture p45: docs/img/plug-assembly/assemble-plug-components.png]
assemble-plug-components


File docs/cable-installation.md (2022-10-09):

# Cable Installation

## Installation

1. Identify the transducer end of the cable.
1. Pre-bend the IDC connector so that the sockets are coaxial with the cable.
1. Hold the cable so that the polarity indicators (embossed triangle / red wire) are on the left.
1. Push the IDC connector onto the PCB header pins.
1. Secure the cable to the transducer housing using the strain rleief clip and M3 x 5 mm socket head screws. Make sure the clip grips the sheathed part of the cable, and not the individual wires.

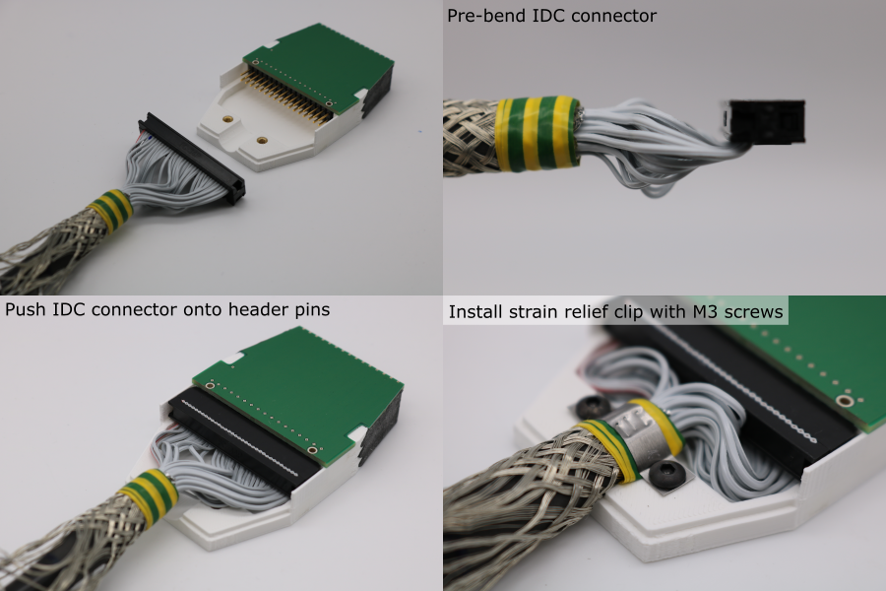
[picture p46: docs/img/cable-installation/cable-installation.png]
cable-installation


## Cable Cover Welding

1. 3D-print the cable cover (orientation and slicer settings detailed in [3D-print-spec.pdf](https://github.com/morganjroberts/open-UST/blob/main/hardware-distribution/3D-print-spec.pdf)).
1. Setup a soldering iron with a temperature of 275 °C and a very clean tip. Setup an extraction fan.
1. Hold the cover piece in place. Make sure that the copper braid is not caught in the cover-housing seam.
1. Tack weld the cover-housing seam using the soldering iron.
1. Fully weld the cover-housing seam, pushing the tip deep into the seam to achieve good penetration.
1. Smooth out the welded seam using the soldering iron tip.

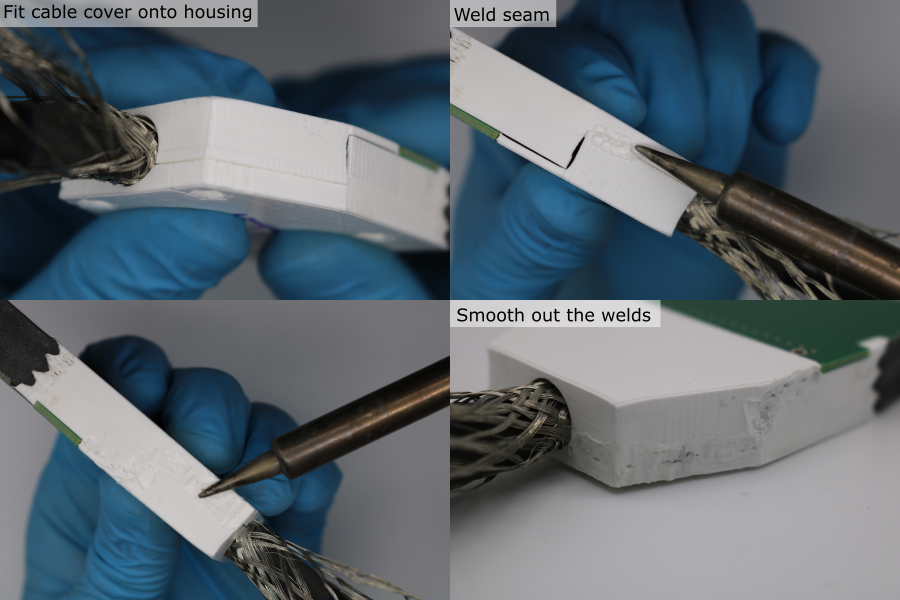
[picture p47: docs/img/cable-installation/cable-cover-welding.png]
cable-cover-welding


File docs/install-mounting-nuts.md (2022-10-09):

# Install Mounting Nuts

## Mounting Nut Preparation

1. Tape a piece of P180 grit sandpaper to a flat glass plate.
1. Abrade each side of the mounting nut by holding it flat against the sandpaper and rubbing in a figure-of-8 pattern. 
1. Put the mounting nuts in a bath of isopropyl alcohol and agitate to degrease them.
1. Thread each mounting nut onto an M3 x 30 mm screw. The threads should engage by ~4 mm.

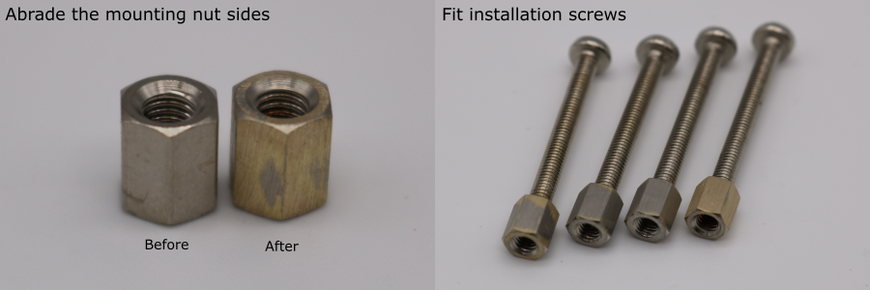
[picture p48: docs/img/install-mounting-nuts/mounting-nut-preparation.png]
mounting-nut-preparation


## Mounting Nut Installation

**Note:** the Loctite 3090 has an extremely short work time, so these steps must be performed very quickly. Make sure that the supplies are prepared before starting, and use two operators.

1. Setup a glass plate on the edge of a workbench and prepare some small G-clamps.
1. Place the transducer module on a flat surface, with the mounting nut recesses facing up.
1. Fit a nozzle to the Loctite 3090 syringe barrel, squeezeout ~0.5 ml of adhesive and discard it.
1. Quickly, dispense a small drop of Loctite 3090 into the bottom of the mounting nut recess. 
1. Spread it around with a wooden cocktail stick to cover the entire bottom face.
1. Dispense Loctite 3090 on to all six sides of the mounting nut.
1. Push the mounting nut into the recess, and remove the screw.
1. repeat this for all 4 mounting nuts in the transducer module.
1. Clamp the transducer module to the glass plate using a small G-clamp, with the mounting nuts facing down. Make sure that the end of each mounting nut is flat against the glass.
1. Allow the adhesive to cure for 1 hour before removing the transducer from the glass plate.

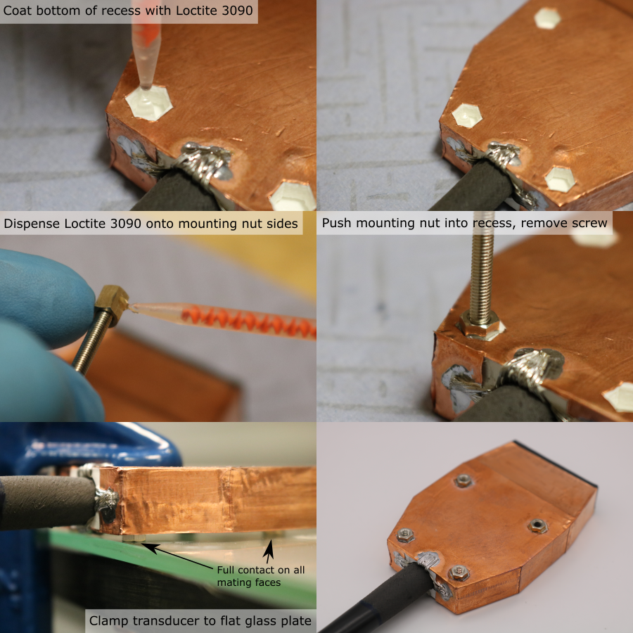
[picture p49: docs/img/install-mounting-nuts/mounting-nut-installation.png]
mounting-nut-installation


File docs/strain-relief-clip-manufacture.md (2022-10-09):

# Strain Relief Clip Manufacture

The strain relief clips are used to secure the cable to the transducer module housing, and to secure the cable to the plug backshell.

## Mark Hole and Outline Locations

1. Download and print the template.
1. Cut a piece of 0.2 mm steel shim stock slightly larger than the template printout, using a guillotine or scissors.
1. Use a pritt stick adhesive to fix the paper template to the steel sheet.

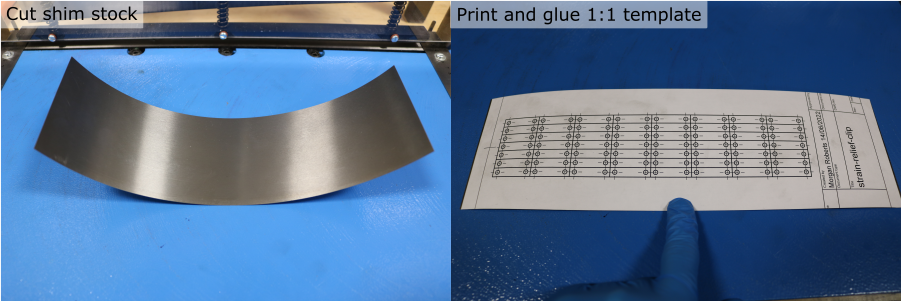
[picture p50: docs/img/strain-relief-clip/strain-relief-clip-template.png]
strain-relief-clip-template


## Drill Holes

1. Clamp the steel sheet to a sacrificial flat surface e.g. perspex.
1. Mount a 3 mm flat end mill in a drill press or mill.
1. Align the end mill with one of the template holes. This is easiest when using a milling machine where the table position can be fixed, or adjusted in the x and y positions.
1. Advance the quill slowly and use light pressure to make the hole. Remove any chips stuck to the cutting face of the end mill before the next hole.
1. Repeat for all the hole locations.

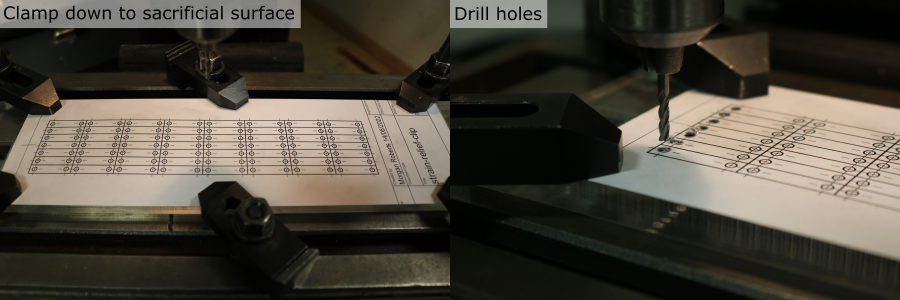
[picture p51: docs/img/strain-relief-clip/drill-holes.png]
drill-holes


## Cut Individual Clip Blanks

1. Use a guillotine or scissors to cut the outlines, forming individual clip blanks

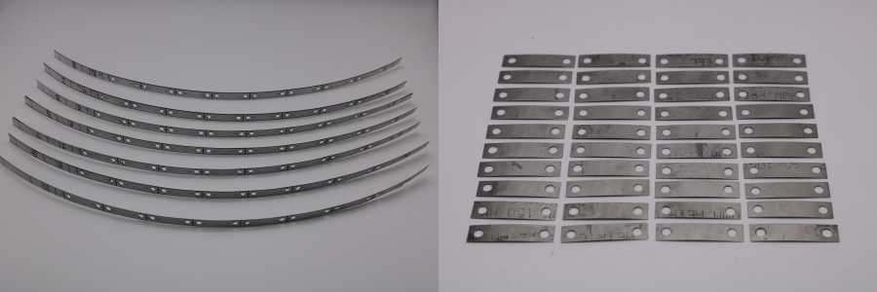
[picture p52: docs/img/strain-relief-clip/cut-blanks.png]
cut-blanks


## Shape the Indents

1. Position a flat head screwdriver in the centre of the clip blank and hit it with a hammer to form an indent.
1. Repeat this to form a total of three indents, with the screwdriver re-positioned above and below the first dent.

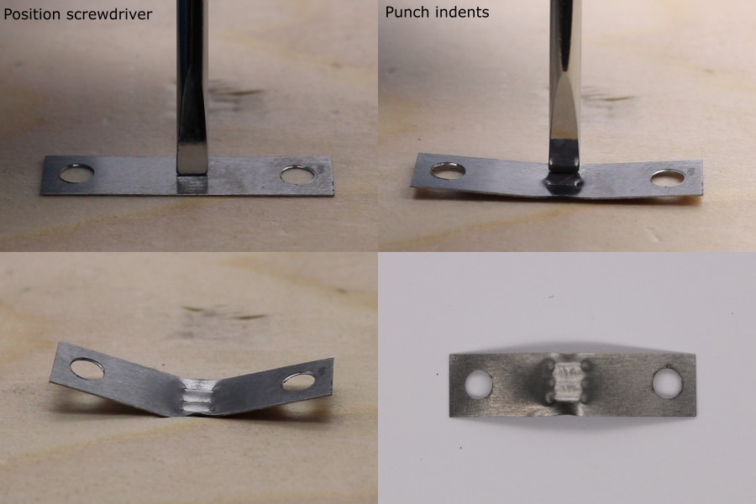
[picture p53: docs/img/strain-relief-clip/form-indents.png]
form-indents


## Shape the Wings

1. Use flat long nose pliers to grip the centre section of the clip.
1. Bend the sides around the pliers to form an overall angle of approximately 90°.
1. Re-position the pliers to cover one of the holes.
1. Bend the wing to an angle of approximately 135°.
1. Repeat for the other wing.

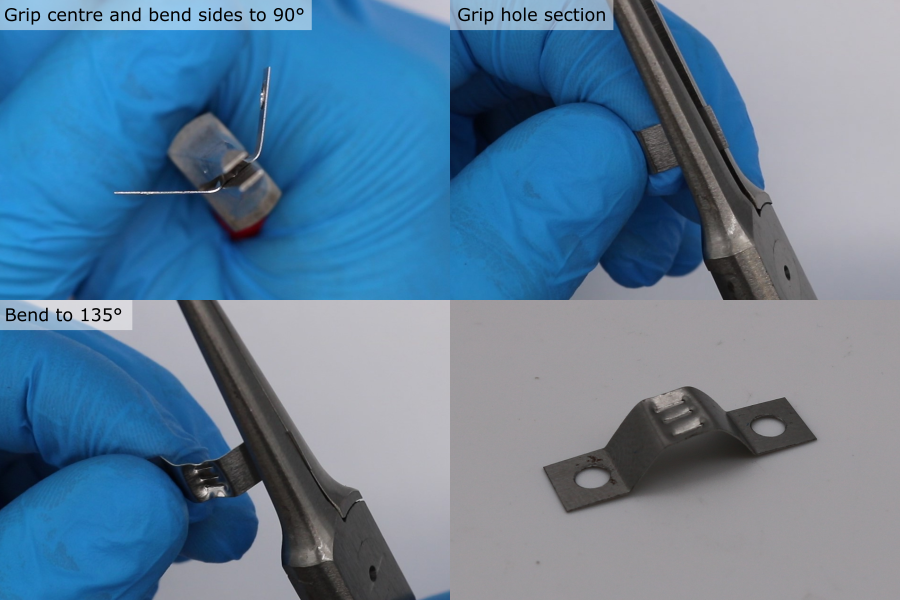
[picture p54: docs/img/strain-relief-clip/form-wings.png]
form-wings


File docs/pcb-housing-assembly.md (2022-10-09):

# PCB-Housing Assembly

## Solder Interconnect PCB

1. Setup a soldering iron with a temperature of 350 °C and a small tip.
1. Position x1 Samtec header pin strip on the interconnect PCB. The edge of the insulating body should be flush with the upper edge of the PCB.
1. Solder the header pin strip to the PCB.

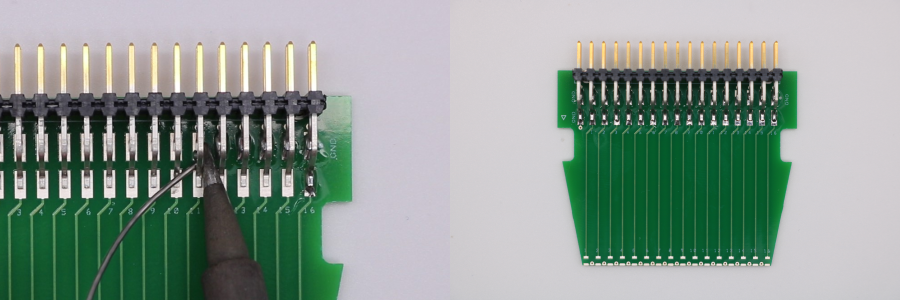
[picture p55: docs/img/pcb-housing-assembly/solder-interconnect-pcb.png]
solder-interconnect-pcb


## Prepare the Housing

**Note:**  Residual PVA can be gently removed from the housing using a toothbrush and foam swabs. Do not use warm water since this can warp the housing.

1. Calibrate the offsets required for the housing (offset calibration process described [here](dimension-calibration-3D-printing.md#housing)).
1. 3D-print the housing (orientation and slicer settings detailed in [3D-print-spec.pdf](https://github.com/morganjroberts/open-UST/blob/main/hardware-distribution/3D-print-spec.pdf)).
1. Allow the parts to cool and remove from the build plate.
1. Remove the PVA support from the wedged structure on the front of the housings. Do not attempt to dig the PVA support out of the mounting nut recesses.
1. Place the housings in a bath of room temperature water for ~36 hours.
1. Install M3 threaded inserts into the housing, using a soldering iron set to 275 °C. Make sure to use a tip that does not protrude all the way through the insert - this would melt a hole through the housing.
1. Use a scalpel to scrape flat the PCB mating face (the region between the two PCB alignment tabs).
1. Test fit the PCB-housing assembly (with the header pin strip facing the housing), to verify that the mating faces are in full contact.
1. Test that the hex nuts seat properly into the hex nut recesses. The hex nut should protrude from the surface by 2 mm. Discard the housing if this fetaure has a defect.

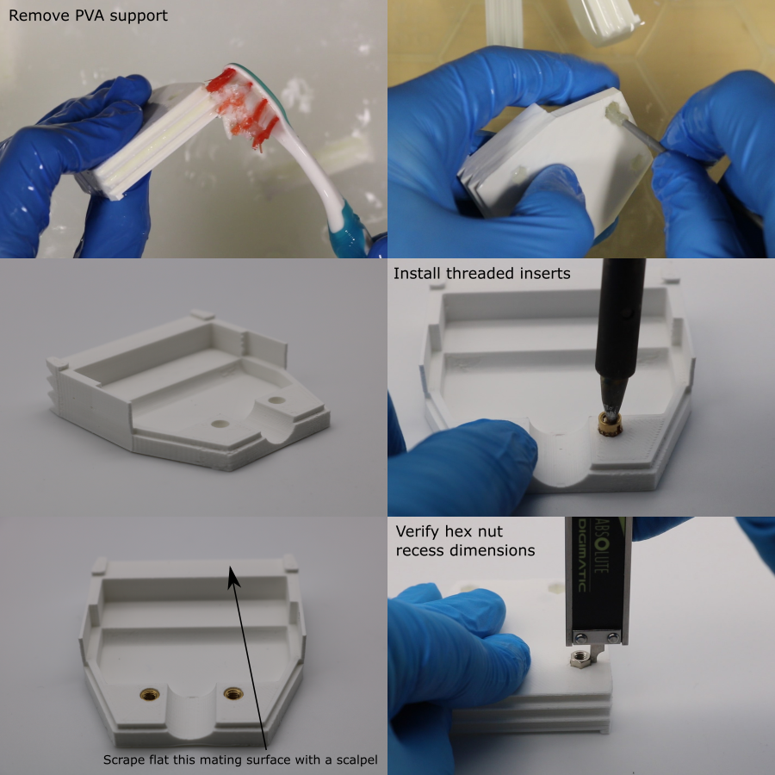
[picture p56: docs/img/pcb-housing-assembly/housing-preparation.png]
housing-preparation


## Base Plate Setup

It is required that the PZT elements are aligned perpendicularly to the top surface of the transducer housing. To achieve this, the PZT elements are placed in the PZT alignment mould to align them perpendicularly with the base plate, which acts as a reference plane. The top surface of the housing is parallel with the surface of the base plate, which in turn means that it is perpendicular to the PZT elements. The following adjustment procedure is required to make the top surface of the housing parallel with the surface of the base plate:

1. Manufacture the base plate assembly (further details [here](custom-tooling-manufacture.md)).
1. Install M3 x 12 mm socket head screws into the threaded holes in the base plate.
1. The initial height of the top of the socket head above the base plate should be approximately 8 mm. Measure this using digital calipers and adjust if necessary (1 rotation advances the M3 screw by 0.5 mm).
1. Clip the PCB to the housing, and place the PCB flat against the base plate, with the housing resting on the socket screws.
1. Push M5 x 30 mm screws through the clamp, into the threaded holes in the base plate. 
1. Tighten the screws to clamp the PCB-housing assembly to the base plate.
1. Use digital calipers to measure the distance between the top of the housing and the top of the base plate. Take two reference measurements at the front of the housing, and calculate the mean of these. This is the target value.
1. At the rear of the housing, record two height measurements: one beside each socket screw.
1. Calculate the difference between each rear measurement and the target value. This is the estimated height adjustment needed for each socket head screw.
1. Remove the clamp and PCB-housing assembly from the base plate, and adjust the screw heights.
1. Verify the adjustment by clamping the PCB-housing assembly to the base plate again, and re-measuring the heights.
1. Repeat this process until the 4 height measurements are within 25 \(\mu m\).
1. Loosen the clamp screws so that the PCB-housing assembly can be removed. Leave the screws and clamp attached to the base plate, for the PCB-housing bonding. 

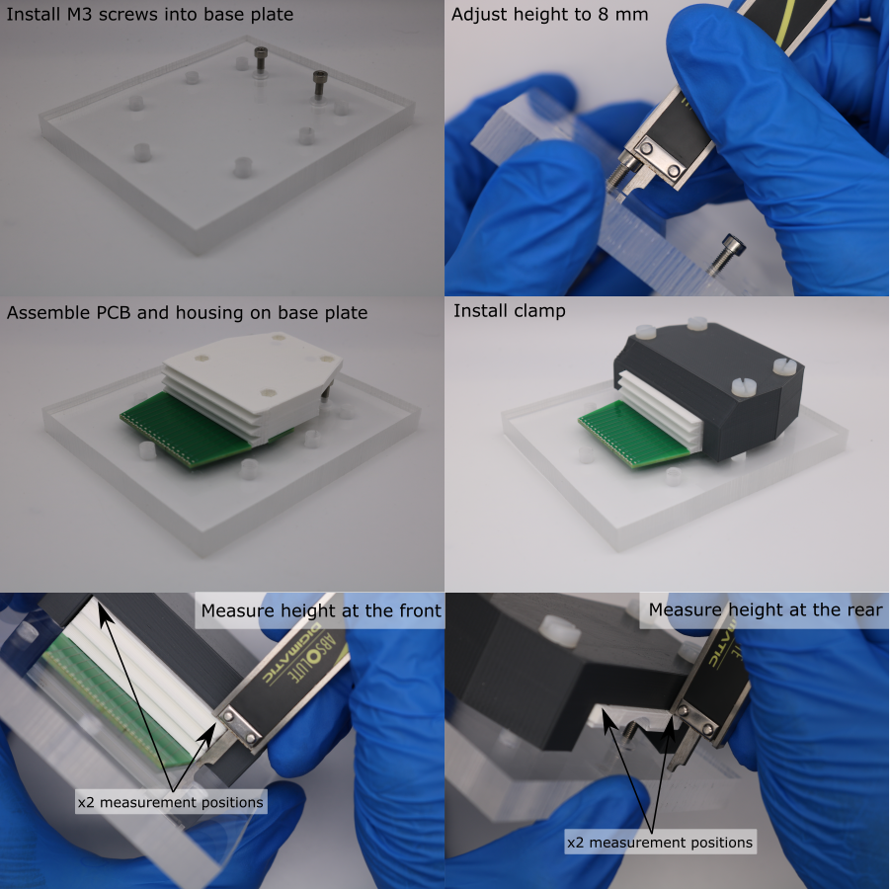
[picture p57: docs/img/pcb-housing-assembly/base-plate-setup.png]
base-plate-setup


## PCB-Housing Bonding

**Note:** the Loctite 3090 has an extremely short work time, so these steps must be performed quickly. Make sure that everything is prepared before starting.

1. Degrease the mating faces on the PCB and the housing with isopropyl alcohol and a foam swab.
1. Fit a nozzle to the Loctite 3090 syringe barrel, squeezeout ~0.5 ml of adhesive and discard it.
1. Dispense a line of adhesive on the mating face of the housing.
1. Clip the interconnect PCB into place.
1. Quickly, place the PCB-housing assembly back on the base plate, sliding it underneath the clamp.
1. Tighten the screws so that the clamp pushes down on the housing.
1. Allow to cure for 1 hour. Do not remove the assembly from the base plate, since this setup is needed again for the rear electrode connection procedure.

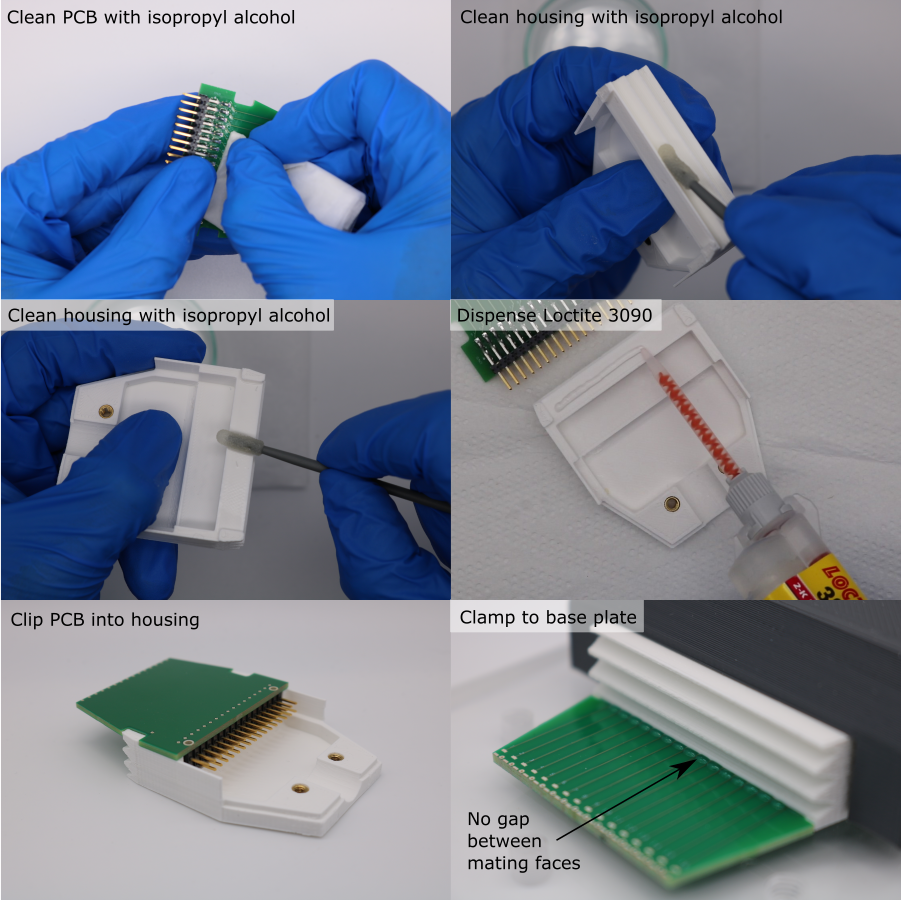
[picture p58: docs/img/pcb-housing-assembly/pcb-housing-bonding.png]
pcb-housing-bonding


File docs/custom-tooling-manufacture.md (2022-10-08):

# Custom Tooling Manufacture

Custom tooling has been designed to enable the low cost manufacture of the open-UST transducers:

- Base plate assembly
- PZT storage tray
- Angled support stand
- Matching layer trimmer
- Matching layer deposition tooling
- Blade coater
- Coating mould strongplate
- Copper foil cutout template
- Vertical transducer clamp
- Breakout PCB soldering jig
- Cable mount PCB soldering jig

Pages in this section are a work-in-progress, and will soon be populated with guidance on how to manufacture these parts.

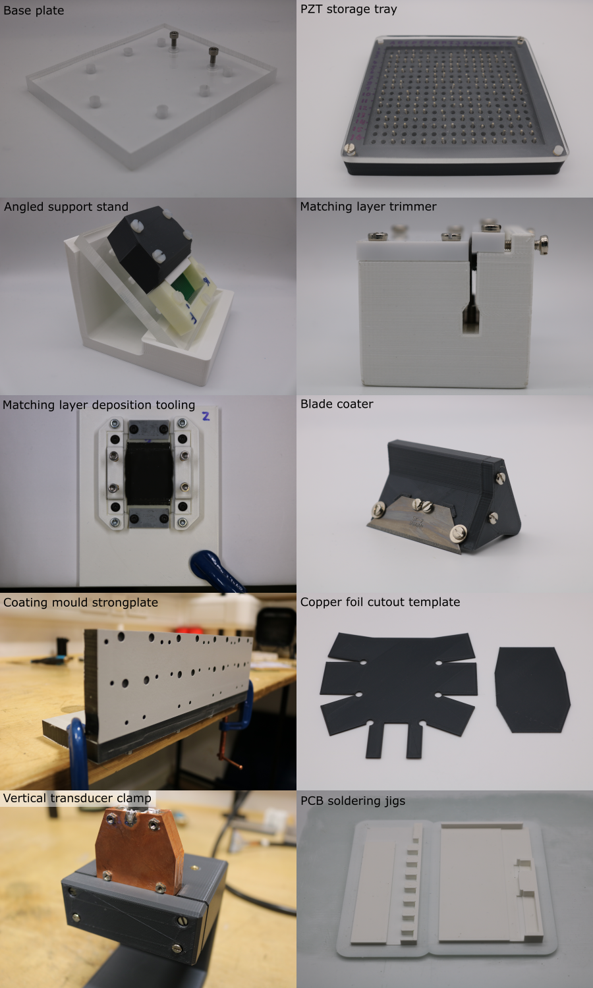
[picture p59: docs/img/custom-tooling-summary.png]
custom-tooling-summary


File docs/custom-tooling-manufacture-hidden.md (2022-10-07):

# Custom Tooling Manufacture

# Test1

Base Plate
clamp
strong plate
angled support plate
matching layer trimmer
doctor blade coater
glass holding jig
PCB soldering jig
pzt storage tray
pzt clean tray

## Manufacture Doctor Blade Coater
The doctor blade coater uses a 3D-printed blade holder to hold a safety blade at the correct angle. It is used during the deposition of the matching layers to scrape the tungsten-epoxy compound over the PZT elements.

doctor-blade-coater

### Set the Blade Height
**Note:** This step is only required if a non-standard PZT thickness is being used: If the nominal PZT thickness is approximately equal to the default value of 1 mm, skip this step and use the default `blade-holder.stl` and `support-arm.stl` files instead.

During use, the angle of the blade is maintained by the support arm, which rides along the surface of the glass plate. For the support arm to have the correct vertical offset from the blade tip, the blade height must be defined as a parameter.  
The blade height should be equal to the thickness of the matching layer deposition mould.  

doctor-blade-coater-blade-height

* Open the `QWML-deposition-mould.f3d` CAD file in Fusion 360.
* Record the `calculated_part_height` value from the `Solid > Modify > Change Parameters` menu,
* Open the [`doctor-blade-coater.f3d`](https://github.com/morganjroberts/open-UST/blob/main/hardware-distribution/doctor-blade-coater/`doctor-blade-coater.f3d`) CAD file in Fusion 360,
* In the `Solid > Modify > Change Parameters` menu, set the `blade_height` parameter to the same value as `calculated_part_height`.
* Export the blade holder and support arm as .stl files.

**Notes:** This doctor blade coater is designed for a specific safety blade (RS PRO 546-758m, part ID XX in BOM). If a different blade is used, the blade dimensions should be updated in the `Change Parameters` menu. The default `blade-angle` parameter used is 45 degrees. Preliminary testing showed that steeper blade angles produce a rougher surface finish, and that shallower blade angles require excessive downwards pressure, which can lead to blade-flexing and non-uniform matching layer thickness.

### 3D-printing

* Load `blade-holder.stl` and `support-arm.stl` into the Cura slicer software.
* Use the following print orientation, to make sure the blade-holding features are flat. Use the 'Select face to align to the build plate' function.

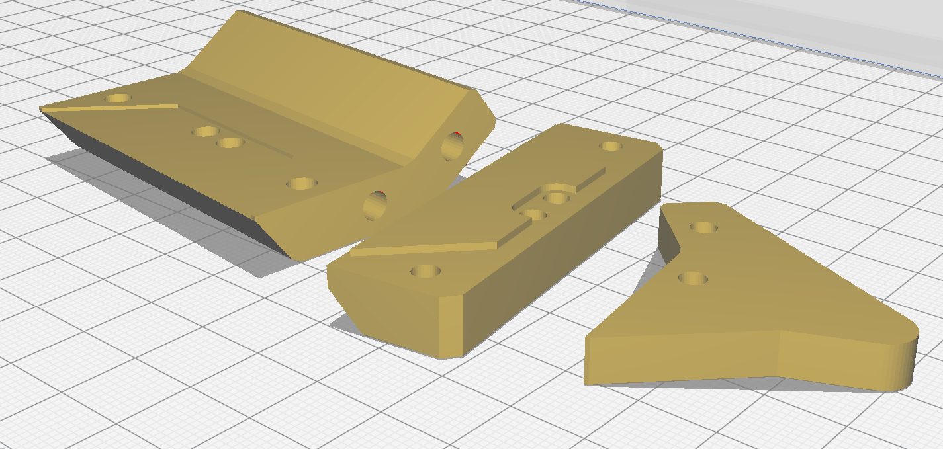
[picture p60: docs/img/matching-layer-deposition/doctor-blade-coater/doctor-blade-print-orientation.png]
doctor_blade_coater_print_orientation


Recomended Settings:

* Use 100% infill to make the blade-holder as stiff as possible, so that the blade can be clamped flat,
* PVA support required for `blade-holder.stl` but not for `support-arm.stl`.
* 0.2 mm layer thickness,
* Enable top support interface.

### Process the Blade-holder

* A smooth flat surface is required to clamp the blade without flexing,
* Use a scalpel to remove bumps created by the 3D-printer nozzle. 

<div align="center">    
    <iframe width="560" height="315" src="https://www.youtube.com/embed/OjL9OB76LAg" title="YouTube video player" frameborder="0" allow="accelerometer; autoplay; clipboard-write; encrypted-media; gyroscope; picture-in-picture" allowfullscreen></iframe>
</div>
<br/>

### Install Threaded Inserts

* Use a soldering iron set to 275 degC,
* Place the M3 threaded insert [part ID 0] on to the soldering iron tip,
* Place the insert into the hole and push gently,
* As the plastic melts, push the insert into the hole, making sure that the insert is properly aligned.
* Keeping pushing until the insert sits below the surface,
* Gently twist the solering iron to remove it.
* Once all the inserts are installed, remove the raised edge around the insert by scraping with a scalpel.

### Install the Safety Blade

* Degrease the blade using Isopropyl Alcohol and a paper towel.
* Attach the support-arm to the blade-holder using x2 of M3 x 12 mm screws [part ID 1].
* Pre-install x4 of M3 x 6 mm screws [part ID 2] into the blade holder, leaving space for the blade. Use washers [part ID 3] for the two outermost screws near the blade tips.
* Slide the safety blade underneath the heads of the screws. Make sure the blade is fully seated against the registering features.
* Gently tighten the screws, using the lowest tension required to grip the blade. Overtightening will lead to blade flex.
* Look along the blade to check its straightness. If there is a visible bend, check that the screws are not overtightened, and that the clamping surfaces are flat and clean.

## PZT storage tray

**Note:** The default stl file is [`PZT Element Tray 16x17 10 mm length.stl`](https://github.com/morganjroberts/open-UST/blob/main/hardware-distribution/pzt-element-tray/PZT%20Element%20Tray%2016x17%2010%20mm%20length.stl), which is a 16 \(\times\) 17 grid, supporting 272 PZT bars of dimensions 1 mm \(\times\) 1 mm \(\times\) 10 mm. To design a tray for more elements, or for elements with different dimensions, open the [`pzt-element-tray.f3d`](https://github.com/morganjroberts/open-UST/blob/main/hardware-distribution/pzt-element-tray/pzt-element-tray.f3d) CAD file in Fusion 360 and edit the `Nrows, Ncolumns, hole_diameter, pzt_element_length` parameters in the `Solid > Modify > Change Parameters` menu.

1. Print the stl file with these settings:
    * Low infill < 20% (non-structural)
    * Coarse layer height 0.2 mm
    * No support required
    * Preview the part and make sure the holes are empty

2. Install the threaded inserts into the holes using a soldering iron set to 275\(^{\circ}\)C (adjust as necessary for non-PLA filaments),
3. Manufacture a perspex lid with 4 mm clearance holes. If using the default stl file, the [`PZT Element Tray Drawing.pdf`](https://github.com/morganjroberts/open-UST/blob/main/hardware-distribution/pzt-element-tray/PZT%20Element%20Tray%20Drawing.pdf) drawing can be printed out at 100% size to help mark out the hole pattern.
4. Label the rows with numbers and columns with letters using a permenant marker.

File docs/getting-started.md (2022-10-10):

# Getting Started

To access the design and manufacture files, clone the GitHub repository locally:

```
git clone https://github.com/morganjroberts/open-UST
```

The design and manufacture files are located in the `hardware-distribution` directory.

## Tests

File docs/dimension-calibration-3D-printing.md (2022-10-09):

# Dimension Calibration for 3D-Printed Parts

The following parts are manufactured using filament-deposition 3D-printing, and have critical dimensions that affect the imaging performance of the open-UST system:

- Deposition mould
- PZT alignment mould
- Housing

To make sure that these critical dimensions are achieved, calibration test pieces are used to estimate the required offsets.

Pages in this section are a work-in-progress, and will soon be populated with guidance on how to perform this calibration.

## Deposition Mould
## PZT Alignment Mould
<!-- ## Calibrate Alignment Mould Slot Width
The slot width should be tuned for every transducer module. Slot width calibration should be performed immediately before printing the final alignmnet-mould for a given transducer module, because deviations in 3D-printer filament diameter can cause drift in 3D-printer linewidth over time.

The alignment mould slot width must be as close as possible to the width of the PZT elements. This is so that the PZT elements cannot rotate in their slots.

These other parameters must be controlled to minimise the gap between the PZT elements and the alignment mould, so that the PZT element location is well known:
- PCB offset
- slot corner radius
- slot length
- 

Tune the slot width:
- print `piece.stl`
- choose the two elements with the largest width
- insert the pzt elements into all of the slots. The element should seat easily into the slots without needing force, but it should not rotate in the slots. -->
## Housing

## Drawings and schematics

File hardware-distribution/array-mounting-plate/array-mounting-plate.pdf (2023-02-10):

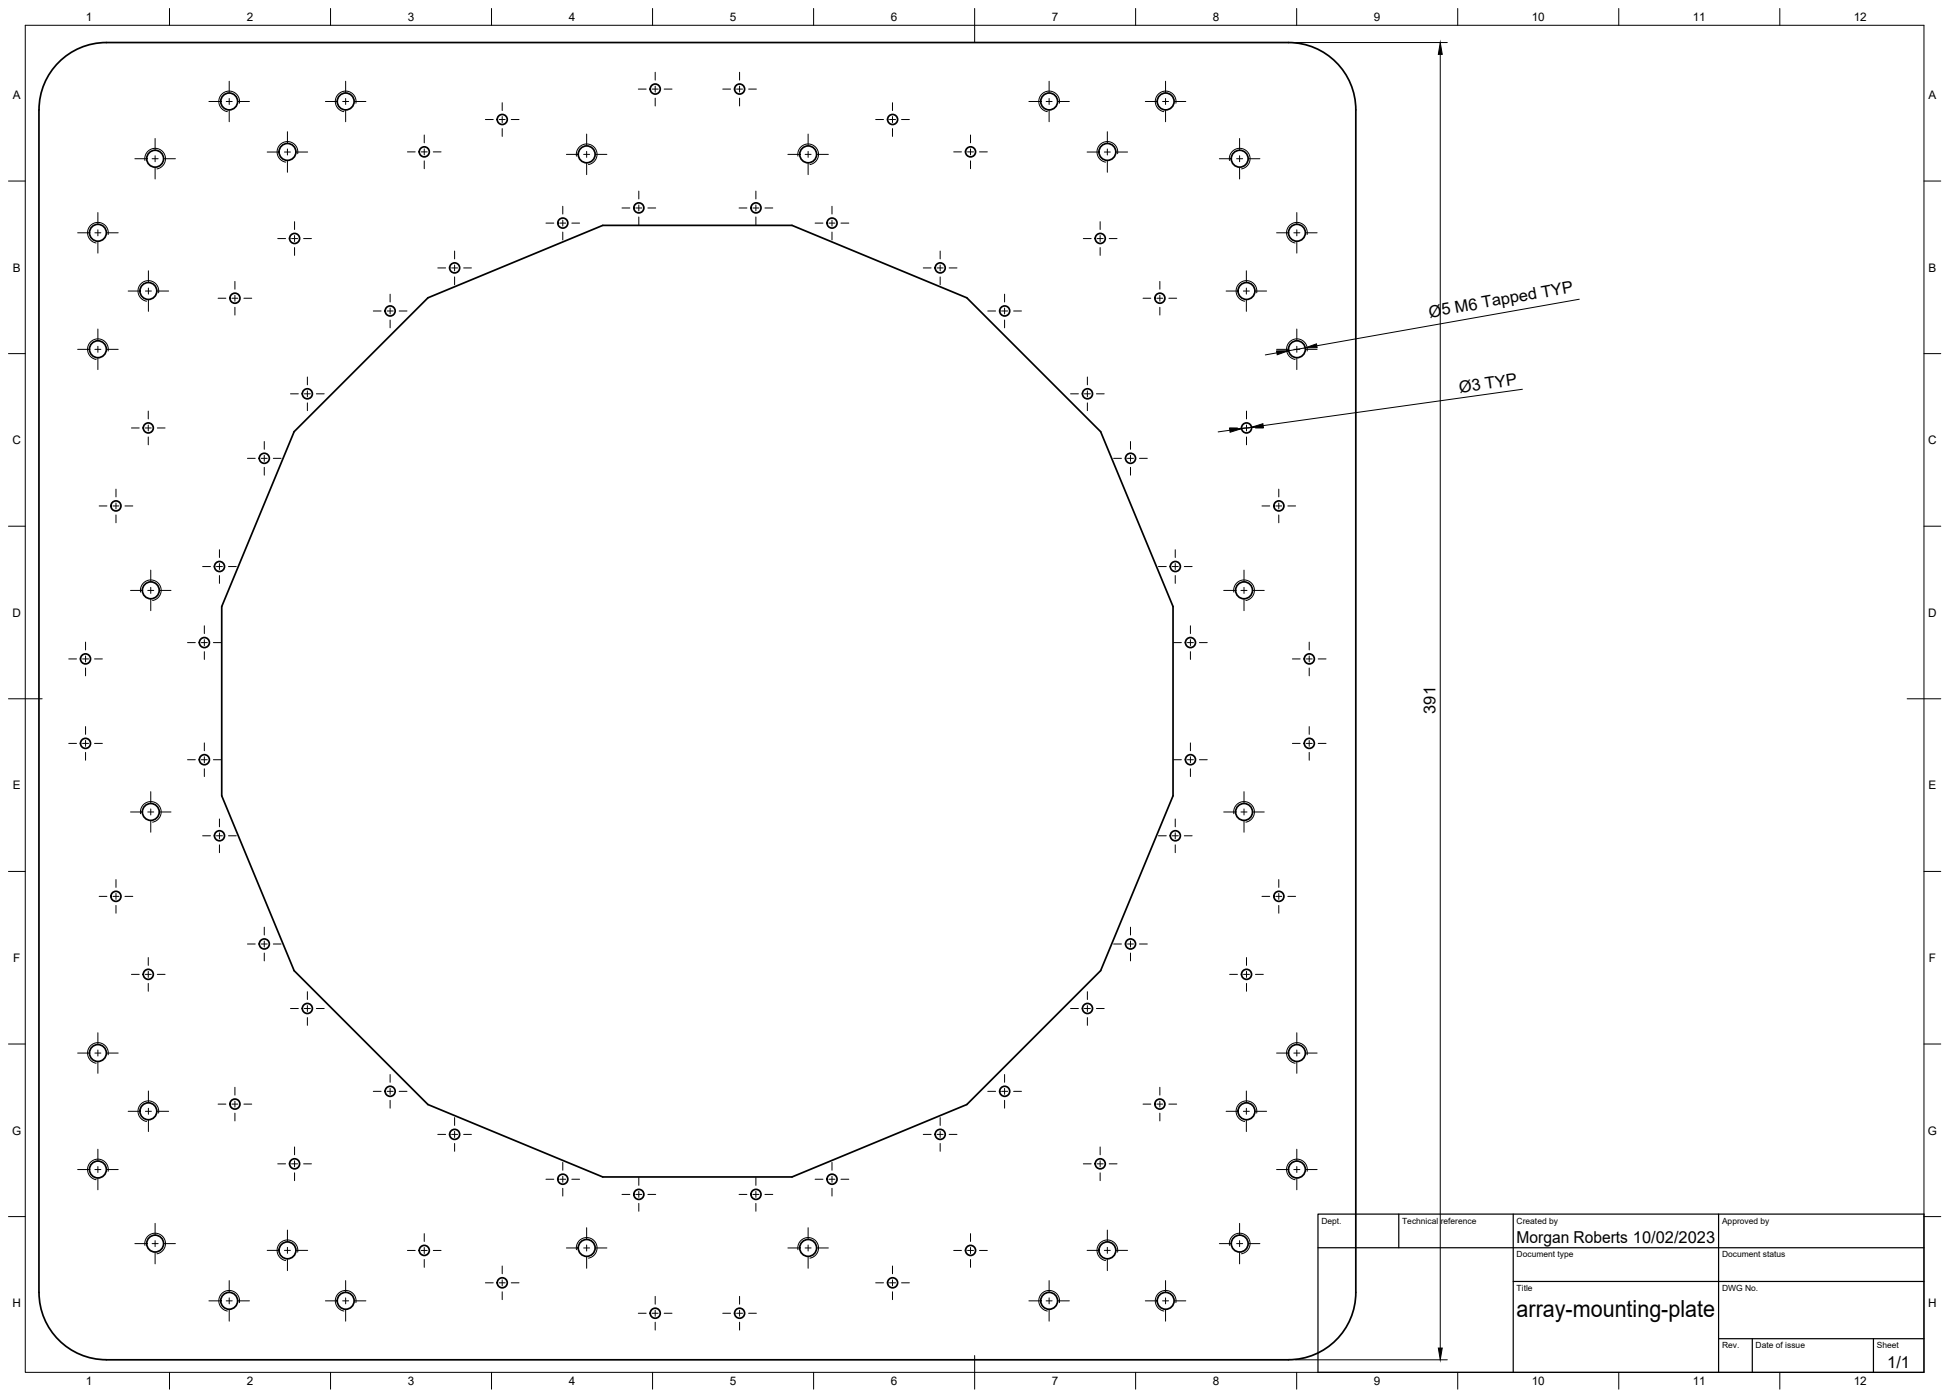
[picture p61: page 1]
Morgan Roberts 391; Ø3 TYP; Ø5 M6 Tapped TYP

Dept. | | Technical reference | Created by 10/02/2023 | Approved by

Document type | Document status

Title array-mounting-plate | DWG No.

Rev. | Date of issue | Sheet 1/1

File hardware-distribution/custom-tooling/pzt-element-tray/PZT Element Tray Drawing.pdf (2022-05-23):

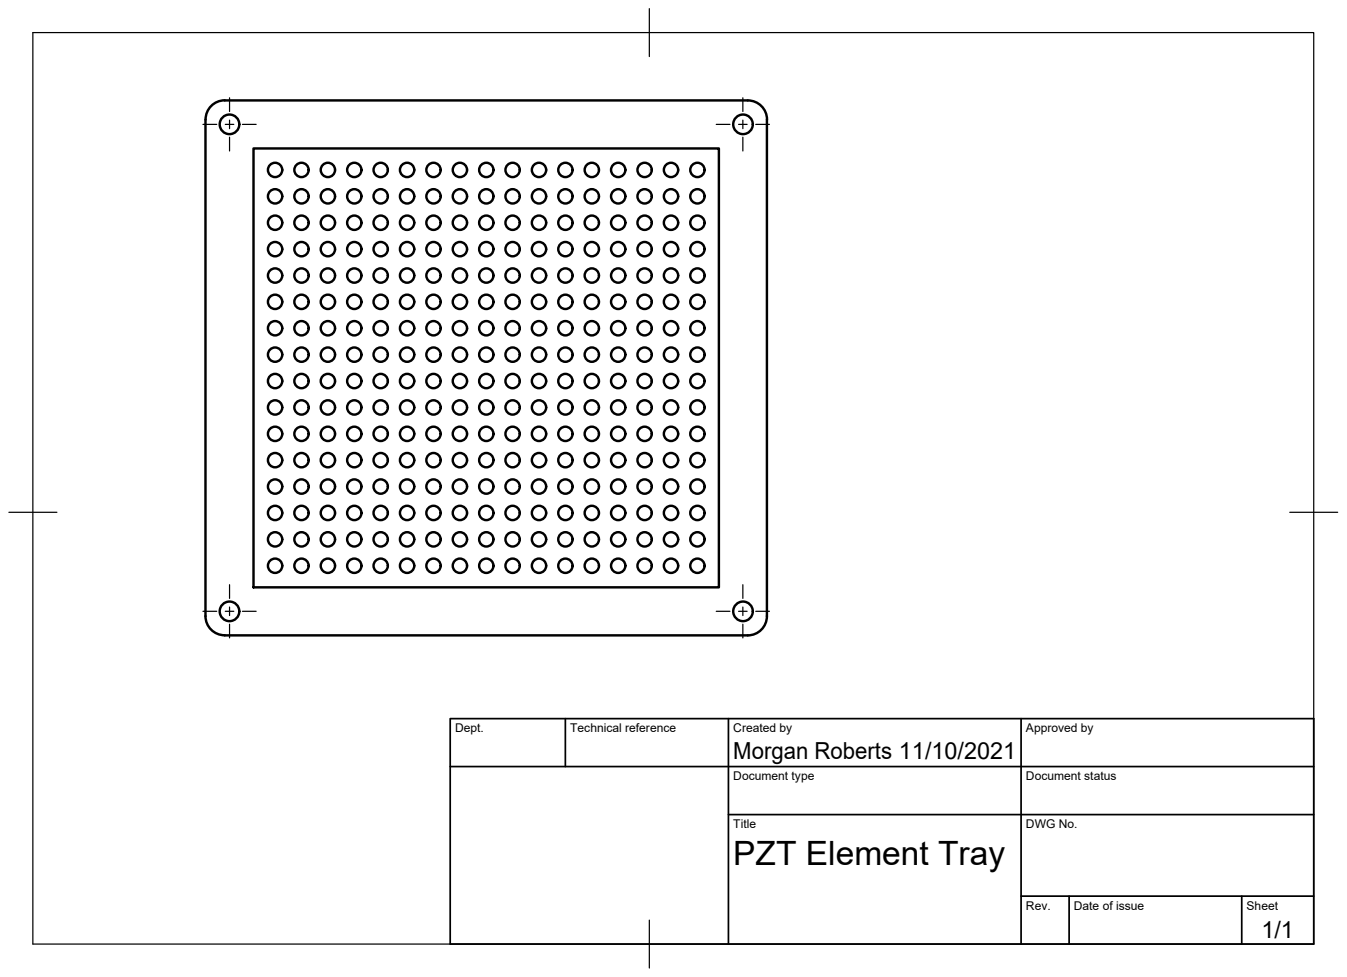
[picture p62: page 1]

Dept. | Technical reference | Created by Morgan Roberts 11/10/2021 | Approved by

Document type | Document status

Title PZT Element Tray | DWG No.

Rev. | Date of issue | Sheet 1/1

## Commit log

2021-10-18 describing slot width calibration
2022-05-18 Update mkdocs.yml
    added 'install mounting points page'
2022-05-18 Update mkdocs.yml
    add 'Housing - PCB bonding' page
2022-05-23 pzt element tray manufacture - commiting to check links work
    [PZT Element Tray 16x17 10 mm length.stl]
2022-05-23 adding pzt element tray 3d files
    [PZT Element Tray 16x17 10 mm length.stl, pzt-element-tray.f3d, pzt-element-tray.step]
2022-05-24 no new material
2022-05-25 adding info on seting blade height for doctor blade coating
    [doctor-blade-coater.f3d, doctor-blade-coater.step]
2022-05-26 adding pzt element electrode folding graphic, chaning pngs to svgs
2022-05-31 changing relative image paths and making hypenation consistent in filenames. Add cable-prep page
2022-06-01 added cable prep pictures
2022-06-02 updating chip-electrode defects image
2022-06-06 adding pzt-dimension-defect spreadsheet and links
    [pzt-element-dimensions-defects.xlsx]
2022-06-06 adding BOM spreadsheet
    [bill-of-materials.xlsx]
2022-06-07 adding composite images to cable-prep page and description
2022-06-10 adding round cable datasheet
2022-06-10 added section on installing IDC connectors
2022-06-15 modified BOM
    [bill-of-materials.xlsx]
2022-07-15 updating BOM with tank mount parts
    [bill-of-materials.xlsx]
2022-10-02 rear electrode connection page
2022-10-06 plug assembly page added
2022-10-09 editing page text up to cable prep
2022-10-10 Adding pics to plug assembly page
2022-10-10 changing BOM to pdf
    [bill-of-materials.xlsx]
2022-10-10 reorganising hardware files
    [PZT Element Tray 16x17 10 mm length.stl, doctor-blade-coater.f3d, doctor-blade-coater.step, pzt-element-tray.f3d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]
2023-02-10 adding PCB files and readme
    [Standard Interconect PCB - Bottom Copper (Paste).gbr, Standard Interconect PCB - Bottom Copper.gbr, Standard Interconect PCB - Bottom Solder Mask.gbr, Standard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]
2023-02-10 PCB readme images
2023-02-10 fixing image links for pcb readme
2023-02-10 fixing image links for pcb readme again
2023-02-10 adding UTA plug files
    [UTA-260-D-plug-backshell.f3d]
2023-02-10 adding UTA plug files stl
    [UTA-260-D-plug-breakout-pcb-retention-bar.stl, UTA-260-D-plug-breakout-pcb-spacer-block.stl, UTA-260-D-plug-clamp-bar.stl, UTA-260-D-plug-coupler.stl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]
2023-02-10 array mounting plate files and readme
    [array-mounting-plate.dxf]
2023-02-10 array bracket files and readme
    [array-mounting-plate.f3d, array-mounting-plate.step, fixed-bracket.stl, sliding-bracket-left.stl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]
2023-02-10 pzt alignment mould folder added
    [PZT Alignment Mould +0.106_sswo_0.55mm_corner_0.075mm_gap.stl, PZT Alignment Mould +0.112_sswo_0.55mm_corner_0.075mm_gap.stl, PZT Alignment Mould +0.118_sswo_0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]
2023-02-10 updating transducer-module CAD
    [transducer-module.step]
